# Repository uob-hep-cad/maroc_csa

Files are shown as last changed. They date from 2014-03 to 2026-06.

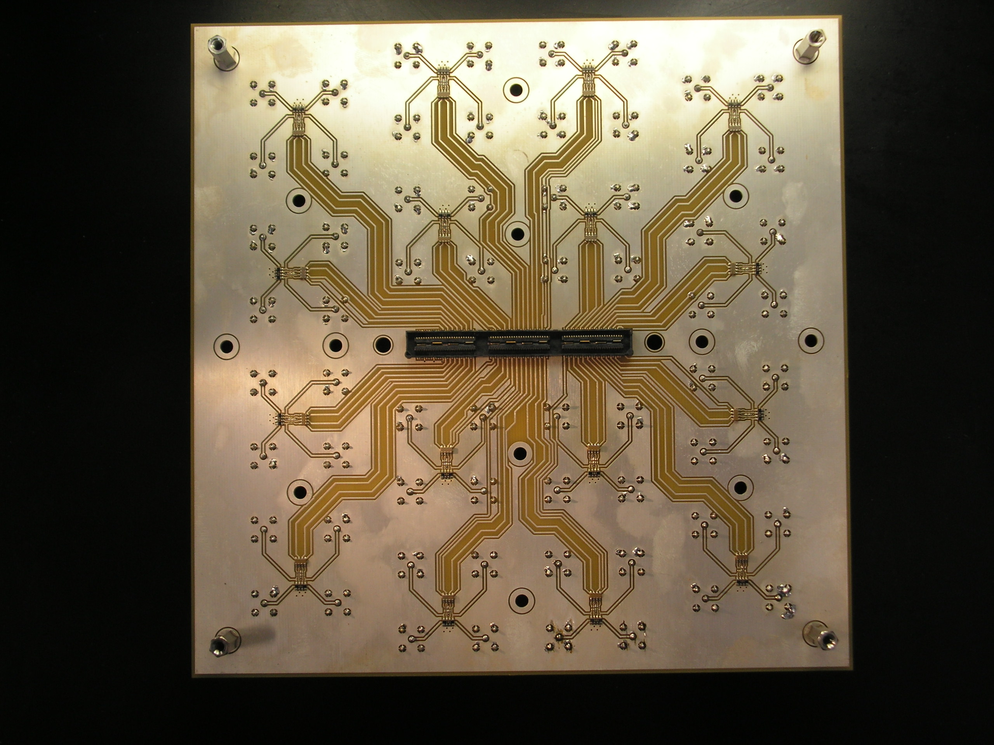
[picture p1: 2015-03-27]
www/Docs/Pictures/pc049a_lemo_adaptor_top_PICT1285.JPG

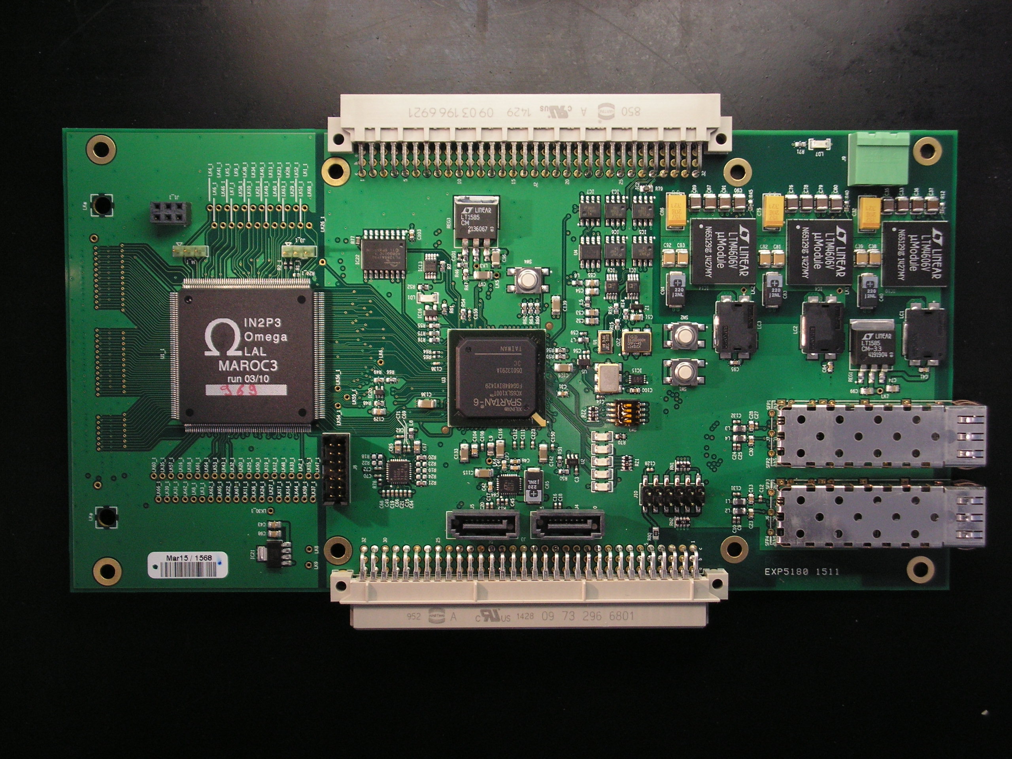
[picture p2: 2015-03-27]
www/Docs/Pictures/pc049a_top_PICT1282.JPG

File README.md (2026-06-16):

# PCB CAD and firmware for pc049a MAROC board

### Two firmware projects:
- `simple` - includes IPBus and MAROC control blocks
- `demo` - includes WhiteRabbit core - currently broken

### To build firmware
* Install Xilinx ISE and a command line environment where `hdlmake` ( from ohwr.org ) works
* pip install hdlmake
* cd firmware/syn/pc049a/simple
* hdlmake
* make

### Software to read out board (Python3)
* cd firmware/scripts
* ./takeMarocData.sh

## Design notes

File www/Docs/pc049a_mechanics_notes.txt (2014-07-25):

Lemo daughter-board
-------------------

Front pannel 3.0mm Aluminium sheet.

EPA connector is 14mm from end to PCB ( 17.0mm overall length )

Want surface flush with top of sheet, or slightly higher

So, stand-offs need to be ( 14mm - 3mm ) = 11mm or less.

For example, use RS 606-686 stand-offs ( M3, stud and thread, body 10mm long ) possibly with washer.

Put mounting holes with same spacing as for SQCD ( see http://www.samtec.com/documents/webfiles/cpdf/XQXX%20WITH%20SCREW-DOWN%20OPTIONS-MKT.pdf )

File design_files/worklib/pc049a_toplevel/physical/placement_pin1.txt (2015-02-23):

UUNITS = MILLIMETERS
SFP1                 19.0000        0.0000       90    TYCO_6367034-1      
SFP3                 0.0000         0.0000       90    TYCO_6367034-1      
SFP2                 21.3300       37.1000       90    TYCO_6367035-1      
SFP4                 2.3300        37.1000       90    TYCO_6367035-1      
IC16                 53.5250      119.4410      270    SOT23_5             
R79                  84.2010       66.6640       90    C0805               
R80                  1.2250        64.9000        0    C0805               
C138                 42.8500      117.6200      270    C0402               
IC21                 -4.8750      152.9000        0    SOT223_5            
R49                  38.9290      130.0970       90    C0603               
R66                  38.9300      127.1800       90    C0603               
R68                  -6.5120      154.6770      180  m C0603               
IC20                 35.1250      131.4000      270    SC70                
REG3                 68.5140      110.2610        0    TO254P1435X460-4N   
U3                   39.4420      102.8530       90    BGA484C100P22X22_2300X2300X260
U5                   44.5046       81.2202      180    SOT23-5             
J4                   4.2510        90.1620        0    SK_SATA_SMD_STR     
J5                   4.2510       110.1620        0    SK_SATA_SMD_STR     
U4                   71.9420       78.8530       90    SOIC8               
RG1_1                51.7900      159.3760       90  m SOT223_4            
R77                  72.5040      135.5830      180    C0402               
R75                  49.9500      116.9400       90    C0603               
R76                  48.3700      118.4300      270    C0603               
IC22                 73.3390      125.0110      180    SOIC127P1030X265-16N
C163                 72.2080       22.3576       90  m C0603               
C164                 72.3604       45.2938       90  m C0603               
C165                 71.7080       -0.4020       90  m C0603               
R11                  70.2014        1.1232       90  m C0603               
J9                   87.1250       10.9000      180    CON2MC_508          
R71                  94.7124       31.8064      270    C0603               
IC5                  72.0920       66.4480      180    SOIC127P600X175-8N  
IC6                  72.0920       72.9480      180    SOIC127P600X175-8N  
IC7                  76.2920       82.7580        0    SOIC127P600X175-8N  
IC2                  81.5920       66.4480      180    SOIC127P600X175-8N  
IC3                  81.5920       72.9480      180    SOIC127P600X175-8N  
REG1                 39.5920       16.0450        0    TO254P1435X460-4N   
C115                 16.8440      107.4090      270    C1206               
C116                 23.9320      102.0990      180    C1206               
C126                 41.9300       85.5200       90    C1206               
C133                 20.0430      110.6080        0    C1206               
C136                 33.3540      120.9980      270    C1206               
C139                 58.0950       88.8910      180    C1206               
C142                 19.9420       91.8530        0    C1206               
C96                  66.2710      103.1150        0    C1206               
C97                  63.7070      104.6630       90    C1206               
R69                  -1.8130      154.6770      180  m C0603               
C127                 39.4420       91.9030      270  m C0402               
C145                 39.4500       99.7550       90  m C0402               
C148                 36.4100      100.7700        0  m C0402               
C151                 55.9120       97.5740        0  m C0402               
C153                 29.6020      113.7830      180  m C0402               
C155                 46.3920      101.8530        0  m C0402               
C157                 42.4420       95.9030      270  m C0402               
C117                 42.4290      105.9090      180  m C0402               
C118                 39.4420      100.9030      270  m C0402               
C119                 39.4500      105.8510       90  m C0402               
R64                  45.4600      117.6200      270    C0402               
R65                  44.4500      117.6100      270    C0402               
C101                 67.5750      111.7510        0    C0402               
C3                   16.5550       83.9320        0    C0402               
C9                   4.8290        45.0010        0    C0402               
C10                  4.8290        46.0170        0    C0402               
C12                  10.8090       39.7940      180    C0402               
C24                  22.4130       46.1060        0    C0402               
C25                  22.4130       45.1060        0    C0402               
C27                  28.3350       40.9370      180    C0402               
C59                  49.9420       82.8030      270    C0402               
C71                  22.9340      124.8810      180    C0402               
C107                 30.4910      102.8610      180  m C0402               
C110                 30.4910       98.7970      180  m C0402               
C51                  53.8350       70.6630      270    C0805               
C52                  52.9420       81.2530      270    C0805               
C53                  54.9420       81.2530      270    C0805               
C54                  59.9420       81.2530      270    C0805               
C55                  61.9420       81.2530      270    C0805               
C65                  23.8840      126.3810      180    C0805               
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
LD7                  94.7886       24.8588       90    D1206               
LD6                  25.4320       79.4480      270    D1206               
LD4                  16.4320       79.4480      270    D1206               
LD3                  19.4320       79.4480      270    D1206               
RN1                  17.6150       59.6450      270    ARC241_SO8          
RN2                  4.1150        59.6450      270    ARC241_SO8          
RZ1                  17.9400       71.1940        0    ARC241_SO8          
RZ2                  29.7020       79.2180        0    ARC241_SO8          
R63                  55.1920       94.8530        0    C0603               
R61                  54.9560      115.3070        0    C0603               
R48                  33.3410      131.5970      270    C0603               
R67                  -3.3610      152.8990        0  m C0603               
R7                   66.6240      115.7630      180    C0603               
R56                  45.9420       88.6030      270    C0603               
R57                  38.8150       62.5900       90  m C0603               
R58                  47.4510       62.5900       90  m C0603               
R59                  44.4420       88.6030      270    C0603               
R60                  55.1920       93.3530        0    C0603               
R62                  55.1900       96.3700        0    C0603               
SW3                  29.2970       68.4020       90    SW_TYCO_1571983-4   
SW1                  42.8470       61.8110       90    OMRON_B3SN-3012     
SW2                  51.4830       61.8110       90    OMRON_B3SN-3012     
SW4                  64.5670       98.9180       90    OMRON_B3SN-3012     
R53                  35.4200      102.1200      270  m C0603               
IC15                 38.3170       68.0350       90    SON50P300X200X100-9N-R175X155
J10                  14.2390       54.7550       90    SAMTEC_TSM-106-01-X-DV
LD2                  22.4320       79.4480      270    D1206               
LD5                  13.4320       79.4480      270    D1206               
LD1                  58.4020      120.8370      270    D1206               
R70                  25.4320       72.6980       90    C0603               
R52                  60.9130      121.0100      270    C0603               
R50                  17.0050       87.6820      270    C0603               
C34                  79.7398        0.5764        0  m C0603               
C88                  80.2906       46.2504        0  m C0603               
J1                   70.7450      198.9860      270  m CON150_QTSDA        
R44                  70.7602       46.7924       90  m C0603               
R51                  20.2550       87.9320      180    C0603               
R46                  66.1200      111.7390      270    C0603               
R47                  64.6600      110.2400      180    C0603               
U2                   20.7496       83.9922      180    SOT23-5             
R32                  29.0570       84.7100        0  m C0603               
R34                  27.8070       86.4600      270  m C0603               
R26                  35.9380       84.7100        0  m C0603               
R28                  34.4380       83.2100        0  m C0603               
R30                  32.0570       84.7100        0  m C0603               
R33                  29.3070       86.4600      270  m C0603               
R35                  25.8070       87.9600      270  m C0603               
R3                   37.4060       83.1760        0  m C0603               
R25                  35.6880       86.4600      270  m C0603               
R27                  34.1880       86.4600      270  m C0603               
R29                  32.6880       86.4600      270  m C0603               
R31                  30.8070       86.4600      270  m C0603               
QZ1                  36.8760       74.3480        0    OSC_SILABS_SI570    
IC1                  58.8330       71.6190        0    SOP65P490X95-8N     
IC9                  58.8330       76.6190        0    SOP65P490X95-8N     
J8                   23.9480      142.0290      270    CON14MD_2MM         
L5                   56.6920       81.3530        0    C0603               
L6                   61.9420       83.1030       90    C0603               
L7                   48.4420       81.6030       90    C0603               
L8                   25.4960      123.2380        0    C0603               
Z1                   55.4460       70.7028        0    SOT23               
QZ2                  45.8720       72.3270        0    OSCSC254P490X696X180-6N
U1                   46.1480       75.9940       90    OSC_4PIN_53S        
R54                  55.3110      110.8530      180    C0603               
R55                  51.7600      118.4300      270    C0603               
R20                  20.4000      120.0600       90    C0603               
R21                  14.3000      120.0600       90    C0603               
R14                  55.3450       72.3060      180    C0603               
R15                  51.4000       74.2860        0    C0603               
R16                  55.1150       74.5920        0    C0603               
R17                  50.6540       67.2260        0  m C0603               
IC11                 14.6110      127.9800        0    QFN50P500X500X100-33N-S355
LC1                  56.0306       -1.2950      180    MURATA_BNX02        
LC3                  57.7324       44.1202      180    MURATA_BNX02        
LC2                  57.5800       23.3430      180    MURATA_BNX02        
C44                  9.2820       102.6070        0    C0402               
C103                 73.9390      122.9560      180    C0603               
C100                 36.4320       70.7850      270    C0603               
C31                  35.6400       87.9900      270    C0603               
C48_1                54.1550      153.2895      270  m C0603               
C52_1                61.5256      146.4027      270  m C0603               
C53_1                19.4830      150.3896      180  m C0603               
C54_1                50.1699      151.2392      180  m C0603               
C48                  19.5100       97.7900       90    C0603               
C41                  41.3470        1.5550      270    C0603               
C95                  43.0488       46.9448      270    C0603               
C84                  41.2896       23.3510        0    C0603               
C42                  14.1570      104.4370      180    C0603               
C46                  17.9870       97.7930       90    C0603               
C13                  11.1090       42.0800      180    C0603               
C23                  6.0530        42.0800        0    C0603               
C28                  28.6350       42.2070      180    C0603               
C30                  23.5790       42.2070        0    C0603               
C47                  19.3100      101.1500      180    C0603               
C33                  81.8518        6.9660      180    CAPC3225X279N       
C35                  81.8360       10.4316      180    CAPC3225X279N       
C36                  81.8574        3.4302      180    CAPC3225X279N       
C37                  81.8614       -0.0586      180    CAPC3225X279N       
C87                  82.4056       52.6154      180    CAPC3225X279N       
C89                  82.4056       56.1154      180    CAPC3225X279N       
C90                  82.4056       45.6154      180    CAPC3225X279N       
C91                  82.4056       49.1154      180    CAPC3225X279N       
C76                  82.2424       33.1900      180    CAPC3225X279N       
C78                  82.2678       29.6848      180    CAPC3225X279N       
C79                  82.2678       26.1796      180    CAPC3225X279N       
C80                  82.2678       22.6744      180    CAPC3225X279N       
C38                  70.7348       16.4274      270    C1210               
C39                  66.7470       16.4274      270    C1210               
C92                  67.2630       62.0700      270    C1210               
C93                  71.3270       62.0700      270    C1210               
C81                  71.1412       39.1858      270    C1210               
C82                  67.1280       39.1604      270    C1210               
J6                   3.7300        26.8000       90    TYCO_1367073        
J7                   22.7300       26.8000       90    TYCO_1367073        
IC13                 68.0580      117.5590      180    SOP65P490X110-8N    
C32                  75.3576       14.9528        0    C7343POL            
C86                  75.9056       60.6154        0    C7343POL            
C75                  75.7386       37.6858        0    C7343POL            
C40                  63.1816       14.7726      180    POSCAP_D3           
C94                  63.4530       60.4430      180    POSCAP_D3           
C83                  63.4102       37.5056      180    POSCAP_D3           
C85                  10.6210       94.0980        0    POSCAP_D3           
L9                   23.3420      104.3530      180    INDC2012X90N        
L1                   9.7240        45.7740      270    INDC2012X90N        
L2                   7.4380        43.9740       90    INDC2012X90N        
L3                   27.2500       45.9010      270    INDC2012X90N        
L4                   24.9640       44.1010       90    INDC2012X90N        
RG1                  11.9912      101.7674        0    QFN50P400X500X80-29N-R375X275
IC10                 68.9314        3.6244      270    LGA133S127P12X12_05-08-1766
IC14                 69.4902       49.2936      270    LGA133S127P12X12_05-08-1766
IC4                  69.3378       26.3574      270    LGA133S127P12X12_05-08-1766
R13                  10.1820      101.5910      180    C0402               
R72                  66.8940       20.0570      180  m C0603               
R73                  67.0210       43.0440      180  m C0603               
R74                  66.3860       -2.6760      180  m C0603               
R10                  75.8910        2.3932       90  m C0603               
R43                  76.4498       48.0624       90  m C0603               
R38                  76.2974       25.1262       90  m C0603               
R12                  80.5526       -2.8272      180    C0603               
R45                  81.1114       42.8420      180    C0603               
R40                  80.9590       19.9058      180    C0603               
R18                  20.6500      132.1400      270    C0603               
R19                  17.3400      120.0600       90    C0603               
R22                  19.1220      132.1110      270    C0603               
R23                  18.8680      120.0700       90    C0603               
R24                  15.8200      120.0700       90    C0603               
R8                   76.7600       -1.3000        0  m C0603               
R9                   75.2760       -2.8030      180  m C0603               
R41                  77.2840       44.4410        0  m C0603               
R42                  75.7840       42.9170      180  m C0603               
R36                  77.1744       21.5060        0  m C0603               
R37                  75.6800       20.0000      180  m C0603               
R39                  70.6078       23.8562       90  m C0603               
LK1                  60.1684       21.3028        0    1-HOLE_0-8P         
LK2                  60.2954       44.2390        0    1-HOLE_0-8P         
LK3                  65.8660      107.6870        0    1-HOLE_0-8P         
LK4                  19.5900      104.6700        0    1-HOLE_0-8P         
LK5                  63.7070      102.9880        0    1-HOLE_0-8P         
LK6                  43.1330      130.4200        0    1-HOLE_0-8P         
LK7                  36.2750       11.2940        0    1-HOLE_0-8P         
LK8                  -1.5790      147.7440        0    1-HOLE_0-8P         
LK9                  -5.3890      147.8710        0    1-HOLE_0-8P         
LK1_1                79.5470      148.2455        0    1-HOLE_0-8P         
LK2_1                16.0470      149.7695        0    1-HOLE_0-8P         
LK3_1                10.4590      173.1375        0    1-HOLE_0-8P         
LK4_1                79.5470      170.5975        0    1-HOLE_0-8P         
LK5_1                79.5470      166.5335        0    1-HOLE_0-8P         
LK6_1                75.4830      169.5815        0    1-HOLE_0-8P         
LK7_1                75.4830      165.5175        0    1-HOLE_0-8P         
LK8_1                10.4590      175.1695        0    1-HOLE_0-8P         
LK9_1                79.5470      164.5015        0    1-HOLE_0-8P         
LK10_1               75.4830      161.4535        0    1-HOLE_0-8P         
LK11_1               10.4590      162.9775        0    1-HOLE_0-8P         
LK12_1               16.0470      155.8655        0    1-HOLE_0-8P         
LK13_1               79.5470      156.3735        0    1-HOLE_0-8P         
LK14_1               10.4590      152.8175        0    1-HOLE_0-8P         
LK15_1               16.0470      147.7375        0    1-HOLE_0-8P         
LK16_1               16.0470      178.2175        0    1-HOLE_0-8P         
LK17_1               10.4590      154.8495        0    1-HOLE_0-8P         
LK18_1               16.0470      176.1855        0    1-HOLE_0-8P         
LK19_1               16.0470      157.8975        0    1-HOLE_0-8P         
LK20_1               16.0470      163.9935        0    1-HOLE_0-8P         
LK21_1               75.4830      159.4215        0    1-HOLE_0-8P         
LK22_1               10.4590      167.0415        0    1-HOLE_0-8P         
LK23_1               79.5470      154.3415        0    1-HOLE_0-8P         
LK24_1               10.4590      158.9135        0    1-HOLE_0-8P         
LK25_1               16.0470      161.9615        0    1-HOLE_0-8P         
LK26_1               66.8470      144.1035        0    1-HOLE_0-8P         
LK27_1               10.4590      156.8815        0    1-HOLE_0-8P         
LK28_1               79.5470      152.3095        0    1-HOLE_0-8P         
LK29_1               75.4830      151.2935        0    1-HOLE_0-8P         
LK30_1               7.6650       156.8815        0    1-HOLE_0-8P         
LK31_1               10.4590      179.4875        0    1-HOLE_0-8P         
LK32_1               16.0470      166.0255        0    1-HOLE_0-8P         
LK33_1               16.0470      151.8015        0    1-HOLE_0-8P         
LK34_1               79.5470      160.4375        0    1-HOLE_0-8P         
LK35_1               16.0470      182.5355        0    1-HOLE_0-8P         
LK36_1               10.4590      160.9455        0    1-HOLE_0-8P         
LK37_1               10.4590      146.7215        0    1-HOLE_0-8P         
LK38_1               79.5470      162.4695        0    1-HOLE_0-8P         
LK39_1               10.4590      181.5195        0    1-HOLE_0-8P         
LK40_1               75.4830      155.3575        0    1-HOLE_0-8P         
LK41_1               79.5470      168.5655        0    1-HOLE_0-8P         
LK42_1               10.4590      177.2015        0    1-HOLE_0-8P         
LK43_1               16.0470      168.0575        0    1-HOLE_0-8P         
LK44_1               10.4590      150.7855        0    1-HOLE_0-8P         
LK45_1               79.5470      158.4055        0    1-HOLE_0-8P         
LK46_1               75.4830      167.5495        0    1-HOLE_0-8P         
LK47_1               16.0470      145.7055        0    1-HOLE_0-8P         
LK48_1               16.0470      153.8335        0    1-HOLE_0-8P         
LK49_1               75.4830      157.3895        0    1-HOLE_0-8P         
LK50_1               16.0470      159.9295        0    1-HOLE_0-8P         
LK51_1               75.4830      149.2615        0    1-HOLE_0-8P         
LK52_1               79.5470      150.2775        0    1-HOLE_0-8P         
LK53_1               16.0470      170.0895        0    1-HOLE_0-8P         
LK54_1               32.8110      140.6255        0    1-HOLE_0-8P         
LK55_1               34.8430      138.4665        0    1-HOLE_0-8P         
LK56_1               36.8750      140.6255        0    1-HOLE_0-8P         
LK57_1               16.0470      180.5035        0    1-HOLE_0-8P         
LK58_1               75.4830      163.4855        0    1-HOLE_0-8P         
LK59_1               10.4590      148.7535        0    1-HOLE_0-8P         
LK60_1               16.0470      184.5675        0    1-HOLE_0-8P         
LK61_1               16.0470      174.1535        0    1-HOLE_0-8P         
LK62_1               10.4590      171.1055        0    1-HOLE_0-8P         
LK63_1               75.4830      153.3255        0    1-HOLE_0-8P         
LK64_1               16.0470      172.1215        0    1-HOLE_0-8P         
LK65_1               10.4590      169.0735        0    1-HOLE_0-8P         
LK66_1               10.4590      183.5515        0    1-HOLE_0-8P         
LK67_1               10.4590      165.0095        0    1-HOLE_0-8P         
LK68_1               75.4830      147.2295        0    1-HOLE_0-8P         
C49                  12.3330      128.8210      180    C0402               
C1                   64.1650      117.5410        0  m C0402               
C2                   76.8920       70.3530        0  m C0402               
C4                   73.5470      126.2810        0  m C0402               
C5                   80.9920       82.8530      180  m C0402               
C6                   67.3920       72.8530        0  m C0402               
C7                   71.3850       83.9380      180  m C0402               
C8                   66.8920       78.8530        0  m C0402               
C14                  34.9420       77.9030       90    C0402               
C15                  12.3400      124.7400      180    C0402               
C16                  8.2660        88.8910        0    C0402               
C17                  8.3930       104.1310        0    C0402               
C18                  8.2660        87.8750        0    C0402               
C19                  12.3330      127.8050      180    C0402               
C20                  8.3010       105.1620        0    C0402               
C21                  12.3330      125.7730      180    C0402               
C45                  9.2820       100.5750        0    C0402               
C60                  49.2000       75.9890      180  m C0402               
C61                  16.8360      120.7510      270  m C0402               
C77                  79.8462       23.3094        0  m C0402               
C128                 17.4420       65.9030       90    C0402               
C130                 47.4510       87.4250      270  m C0402               
C131                 11.5760       45.1730       90    C0402               
C132                 28.9420       45.3000       90    C0402               
C134                 32.4420      106.9030      270  m C0402               
C137                 42.4920      102.8530      180  m C0402               
C140                 40.4500      107.7560       90  m C0402               
C141                 39.8310       88.3140      270  m C0402               
C143                 44.3450      113.7830        0  m C0402               
C144                 31.9570      116.0110       90  m C0402               
C146                 50.4610       92.9880      270  m C0402               
C147                 34.7510      116.0110       90  m C0402               
C149                 23.3790      102.0990      180  m C0402               
C150                 22.3630       89.6530        0    C0402               
C152                 50.3630      102.8690        0  m C0402               
C154                 32.4920      102.8530      180  m C0402               
C156                 37.6030      113.7830      180  m C0402               
C158                 26.1150       95.8180       90  m C0402               
C159                 55.0200      109.3680      180    C0402               
C160                 40.4660      108.8880      270  m C0402               
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
J3_1                 69.3870      152.0555      270    CONHE13D3X1M        
J4_1                 69.3870      177.7095      270    CONHE13D3X1M        
J1_1                 76.9850      176.4995      270    SAMTEC_SSW-103-01-G-D
J2                   95.3650      139.7200        0    HARTING_0903196X921 
J3                   -9.1150       50.8200      180    HARTING_09732966801 
D1_1                 52.8550      148.7395        0  m SOD323_INV          
U1_1                 59.4950      178.9795      270    PQFP240_050         
R20_1                33.0450      157.6995      180  m C0402               
R21_1                35.9450      157.6995        0  m C0402               
R22_1                33.0450      159.6995      180  m C0402               
R23_1                35.9450      159.6995        0  m C0402               
R25_1                31.0324      165.1165      180  m C0402               
R26_1                23.5450      165.1995      180  m C0402               
R28_1                33.9450      162.6995        0  m C0402               
R29_1                35.9450      162.6995        0  m C0402               
R30_1                24.4450      161.1995        0  m C0402               
R31_1                23.5450      162.1995      180  m C0402               
R32_1                31.0476      153.2569      180  m C0402               
R33_1                31.9476      152.0109        0  m C0402               
R34_1                54.4450      171.6995        0  m C0402               
R35_1                53.5450      170.6995      180  m C0402               
R36_1                31.0246      147.7191      180  m C0402               
R37_1                23.5443      148.1433      180  m C0402               
R14_1                35.0625      161.6673      180  m C0402               
R17_1                55.9450      158.6995        0  m C0402               
R78                  14.1400      130.7600        0    C0402               
R1                   81.9420       68.8030       90  m C0402               
R2                   81.9420       75.3030       90  m C0402               
R6                   72.5970       79.9430       90  m C0402               
R24_1                63.7990      150.7275      270    C0402               
R3_1                 58.7835      147.9388        0  m C0402               
R4_1                 23.5443      150.5662      180  m C0402               
R5_1                 31.0476      163.9055      180  m C0402               
R6_1                 56.8478      174.7564        0  m C0402               
R7_1                 55.9450      169.1995        0  m C0402               
R8_1                 31.0450      173.6995      180  m C0402               
R9_1                 55.9353      167.8937        0  m C0402               
R10_1                32.9763      167.1576      180  m C0402               
R11_1                55.9864      166.0878        0  m C0402               
R12_1                24.4450      157.1995        0  m C0402               
R13_1                55.9450      161.6995        0  m C0402               
R15_1                24.4450      154.6995        0  m C0402               
R16_1                24.4450      152.6995        0  m C0402               
R27_1                34.0050      151.3895      180  m C0402               
R46_1                62.9743      146.7405      270  m C0402               
R47_1                19.7509      149.0089      180  m C0402               
R4                   72.2850       82.6680        0  m C0402               
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

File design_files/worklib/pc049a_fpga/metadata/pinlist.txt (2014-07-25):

(Pinlist
	(Pin
		(Name ENABLE_GCLK_DRIVE_O)
		(MSB )
		(LSB )
		(Type OUTPUT)
		(Location Right)
		(InputLoadLow )
		(InputLoadHigh )
		(OutputLoadLow 1.0)
		(OutputLoadHigh -1.0)
		(CheckLoad Both)
		(CheckIO Both)
		(CheckDir 1)
		(CheckAssert 1)
		(CheckOutput 1)
		(UnknownLoading 0)
		(PinShape Line)
		(DIFF_PAIR_PINS_POS )
		(DIFF_PAIR_PINS_NEG )
	)

	(Pin
		(Name ENABLE_GLOBALTRIG_DRIVE_O)
		(MSB )
		(LSB )
		(Type OUTPUT)
		(Location Right)
		(InputLoadLow )
		(InputLoadHigh )
		(OutputLoadLow 1.0)
		(OutputLoadHigh -1.0)
		(CheckLoad Both)
		(CheckIO Both)
		(CheckDir 1)
		(CheckAssert 1)
		(CheckOutput 1)
		(UnknownLoading 0)
		(PinShape Line)
		(DIFF_PAIR_PINS_POS )
		(DIFF_PAIR_PINS_NEG )
	)

	(Pin
		(Name LVDS_GCLK_FROM_FPGA_N_O)
		(MSB )
		(LSB )
		(Type OUTPUT)
		(Location Right)
		(InputLoadLow -0.01)
		(InputLoadHigh 0.01)
		(OutputLoadLow 1.0)
		(OutputLoadHigh -1.0)
		(CheckLoad Both)
		(CheckIO Both)
		(CheckDir 1)
		(CheckAssert 1)
		(CheckOutput 1)
		(UnknownLoading 0)
		(PinShape Line)
		(DIFF_PAIR_PINS_POS )
		(DIFF_PAIR_PINS_NEG )
	)

	(Pin
		(Name LVDS_GCLK_FROM_FPGA_P_O)
		(MSB )
		(LSB )
		(Type OUTPUT)
		(Location Right)
		(InputLoadLow )
		(InputLoadHigh )
		(OutputLoadLow 1.0)
		(OutputLoadHigh -1.0)
		(CheckLoad Both)
		(CheckIO Both)
		(CheckDir 1)
		(CheckAssert 1)
		(CheckOutput 1)
		(UnknownLoading 0)
		(PinShape Line)
		(DIFF_PAIR_PINS_POS )
		(DIFF_PAIR_PINS_NEG )
	)

	(Pin
		(Name LVDS_GCLK_TO_FPGA_N_I)
		(MSB )
		(LSB )
		(Type INPUT)
		(Location Left)
		(InputLoadLow -0.01)
		(InputLoadHigh 0.01)
		(OutputLoadLow )
		(OutputLoadHigh )
		(CheckLoad Off)
		(CheckIO Off)
		(CheckDir 0)
		(CheckAssert 0)
		(CheckOutput 0)
		(UnknownLoading 0)
		(PinShape Line)
		(DIFF_PAIR_PINS_POS )
		(DIFF_PAIR_PINS_NEG )
	)

	(Pin
		(Name LVDS_GCLK_TO_FPGA_P_I)
		(MSB )
		(LSB )
		(Type INPUT)
		(Location Left)
		(InputLoadLow -0.01)
		(InputLoadHigh 0.01)
		(OutputLoadLow )
		(OutputLoadHigh )
		(CheckLoad Both)
		(CheckIO Both)
		(CheckDir 1)
		(CheckAssert 1)
		(CheckOutput 1)
		(UnknownLoading 0)
		(PinShape Line)
		(DIFF_PAIR_PINS_POS )
		(DIFF_PAIR_PINS_NEG )
	)

	(Pin
		(Name LVDS_GLOBALTRIG_FROM_FPGA_N_O)
		(MSB )
		(LSB )
		(Type OUTPUT)
		(Location Right)
		(InputLoadLow -0.01)
		(InputLoadHigh 0.01)
		(OutputLoadLow 1.0)
		(OutputLoadHigh -1.0)
		(CheckLoad Both)
		(CheckIO Both)
		(CheckDir 1)
		(CheckAssert 1)
		(CheckOutput 1)
		(UnknownLoading 0)
		(PinShape Line)
		(DIFF_PAIR_PINS_POS )
		(DIFF_PAIR_PINS_NEG )
	)

	(Pin
		(Name LVDS_GLOBALTRIG_FROM_FPGA_P_O)
		(MSB )
		(LSB )
		(Type OUTPUT)
		(Location Right)
		(InputLoadLow )
		(InputLoadHigh )
		(OutputLoadLow 1.0)
		(OutputLoadHigh -1.0)
		(CheckLoad Both)
		(CheckIO Both)
		(CheckDir 1)
		(CheckAssert 1)
		(CheckOutput 1)
		(UnknownLoading 0)
		(PinShape Line)
		(DIFF_PAIR_PINS_POS )
		(DIFF_PAIR_PINS_NEG )
	)

	(Pin
		(Name LVDS_GLOBALTRIG_TO_FPGA_N_I)
		(MSB )
		(LSB )
		(Type INPUT)
		(Location Left)
		(InputLoadLow -0.01)
		(InputLoadHigh 0.01)
		(OutputLoadLow )
		(OutputLoadHigh )
		(CheckLoad Both)
		(CheckIO Both)
		(CheckDir 1)
		(CheckAssert 1)
		(CheckOutput 1)
		(UnknownLoading 0)
		(PinShape Line)
		(DIFF_PAIR_PINS_POS )
		(DIFF_PAIR_PINS_NEG )
	)

	(Pin
		(Name LVDS_GLOBALTRIG_TO_FPGA_P_I)
		(MSB )
		(LSB )
		(Type INPUT)
		(Location Left)
		(InputLoadLow -0.01)
		(InputLoadHigh 0.01)
		(OutputLoadLow )
		(OutputLoadHigh )
		(CheckLoad Both)
		(CheckIO Both)
		(CheckDir 1)
		(CheckAssert 1)
		(CheckOutput 1)
		(UnknownLoading 0)
		(PinShape Line)
		(DIFF_PAIR_PINS_POS )
		(DIFF_PAIR_PINS_NEG )
	)

	(Pin
		(Name LVDS_OTRIG_FROM_FPGA_N_O)
		(MSB )
		(LSB )
		(Type OUTPUT)
		(Location Right)
		(InputLoadLow -0.01)
		(InputLoadHigh 0.01)
		(OutputLoadLow 1.0)
		(OutputLoadHigh -1.0)
		(CheckLoad Both)
		(CheckIO Both)
		(CheckDir 1)
		(CheckAssert 1)
		(CheckOutput 1)
		(UnknownLoading 0)
		(PinShape Line)
		(DIFF_PAIR_PINS_POS )
		(DIFF_PAIR_PINS_NEG )
	)

	(Pin
		(Name LVDS_OTRIG_FROM_FPGA_P_O)
		(MSB )
		(LSB )
		(Type OUTPUT)
		(Location Right)
		(InputLoadLow )
		(InputLoadHigh )
		(OutputLoadLow 1.0)
		(OutputLoadHigh -1.0)
		(CheckLoad Both)
		(CheckIO Both)
		(CheckDir 1)
		(CheckAssert 1)
		(CheckOutput 1)
		(UnknownLoading 0)
		(PinShape Line)
		(DIFF_PAIR_PINS_POS )
		(DIFF_PAIR_PINS_NEG )
	)

	(Pin
		(Name LVDS_OTRIG_TO_FPGA_N_I)
		(MSB )
		(LSB )
		(Type INPUT)
		(Location Left)
		(InputLoadLow -0.01)
		(InputLoadHigh 0.01)
		(OutputLoadLow )
		(OutputLoadHigh )
		(CheckLoad Off)
		(CheckIO Off)
		(CheckDir 0)
		(CheckAssert 0)
		(CheckOutput 0)
		(UnknownLoading 0)
		(PinShape Line)
		(DIFF_PAIR_PINS_POS )
		(DIFF_PAIR_PINS_NEG )
	)

	(Pin
		(Name LVDS_OTRIG_TO_FPGA_P_I)
		(MSB )
		(LSB )
		(Type INPUT)
		(Location Left)
		(InputLoadLow -0.01)
		(InputLoadHigh 0.01)
		(OutputLoadLow )
		(OutputLoadHigh )
		(CheckLoad Both)
		(CheckIO Both)
		(CheckDir 1)
		(CheckAssert 1)
		(CheckOutput 1)
		(UnknownLoading 0)
		(PinShape Line)
		(DIFF_PAIR_PINS_POS )
		(DIFF_PAIR_PINS_NEG )
	)

	(Pin
		(Name BUTTON1_I)
		(MSB )
		(LSB )
		(Type INPUT)
		(Location Left)
		(InputLoadLow -0.01)
		(InputLoadHigh 0.01)
		(OutputLoadLow )
		(OutputLoadHigh )
		(CheckLoad Both)
		(CheckIO Both)
		(CheckDir 1)
		(CheckAssert 1)
		(CheckOutput 1)
		(UnknownLoading 0)
		(PinShape Line)
		(DIFF_PAIR_PINS_POS )
		(DIFF_PAIR_PINS_NEG )
	)

	(Pin
		(Name BUTTON2_I)
		(MSB )
		(LSB )
		(Type INPUT)
		(Location Left)
		(InputLoadLow -0.01)
		(InputLoadHigh 0.01)
		(OutputLoadLow )
		(OutputLoadHigh )
		(CheckLoad Both)
		(CheckIO Both)
		(CheckDir 1)
		(CheckAssert 1)
		(CheckOutput 1)
		(UnknownLoading 0)
		(PinShape Line)
		(DIFF_PAIR_PINS_POS )
		(DIFF_PAIR_PINS_NEG )
	)

	(Pin
		(Name FPGA_SCL_B)
		(MSB )
		(LSB )
		(Type BIDIR)
		(Location Right)
		(InputLoadLow -0.01)
		(InputLoadHigh 0.01)
		(OutputLoadLow 1.0)
		(OutputLoadHigh -1.0)
		(CheckLoad Both)
		(CheckIO Both)
		(CheckDir 1)
		(CheckAssert 1)
		(CheckOutput 1)
		(UnknownLoading 0)
		(PinShape Line)
		(DIFF_PAIR_PINS_POS )
		(DIFF_PAIR_PINS_NEG )
	)

	(Pin
		(Name FPGA_SDA_B)
		(MSB )
		(LSB )
		(Type BIDIR)
		(Location Right)
		(InputLoadLow -0.01)
		(InputLoadHigh 0.01)
		(OutputLoadLow 1.0)
		(OutputLoadHigh -1.0)
		(CheckLoad Both)
		(CheckIO Both)
		(CheckDir 1)
		(CheckAssert 1)
		(CheckOutput 1)
		(UnknownLoading 0)
		(PinShape Line)
		(DIFF_PAIR_PINS_POS )
		(DIFF_PAIR_PINS_NEG )
	)

	(Pin
		(Name CTEST_O)
		(MSB 5)
		(LSB 0)
		(Type OUTPUT)
		(Location Right)
		(InputLoadLow )
		(InputLoadHigh )
		(OutputLoadLow 1.0)
		(OutputLoadHigh -1.0)
		(CheckLoad Both)
		(CheckIO Both)
		(CheckDir 1)
		(CheckAssert 1)
		(CheckOutput 1)
		(UnknownLoading 0)
		(PinShape Line)
		(DIFF_PAIR_PINS_POS )
		(DIFF_PAIR_PINS_NEG )
	)

	(Pin
		(Name LEDS_O)
		(MSB 4)
		(LSB 0)
		(Type OUTPUT)
		(Location Right)
		(InputLoadLow )
		(InputLoadHigh )
		(OutputLoadLow 1.0)
		(OutputLoadHigh -1.0)
		(CheckLoad Both)
		(CheckIO Both)
		(CheckDir 1)
		(CheckAssert 1)
		(CheckOutput 1)
		(UnknownLoading 0)
		(PinShape Line)
		(DIFF_PAIR_PINS_POS )
		(DIFF_PAIR_PINS_NEG )
	)

	(Pin
		(Name DIP_SWITCH_I)
		(MSB 3)
		(LSB 0)
		(Type INPUT)
		(Location Left)
		(InputLoadLow -0.01)
		(InputLoadHigh 0.01)
		(OutputLoadLow )
		(OutputLoadHigh )
		(CheckLoad Both)
		(CheckIO Both)
		(CheckDir 1)
		(CheckAssert 1)
		(CheckOutput 1)
		(UnknownLoading 0)
		(PinShape Line)
		(DIFF_PAIR_PINS_POS )
		(DIFF_PAIR_PINS_NEG )
	)

	(Pin
		(Name GPIO)
		(MSB 7)
		(LSB 0)
		(Type OUTPUT)
		(Location Right)
		(InputLoadLow )
		(InputLoadHigh )
		(OutputLoadLow 1.0)
		(OutputLoadHigh -1.0)
		(CheckLoad Both)
		(CheckIO Both)
		(CheckDir 1)
		(CheckAssert 1)
		(CheckOutput 1)
		(UnknownLoading 0)
		(PinShape Line)
		(DIFF_PAIR_PINS_POS )
		(DIFF_PAIR_PINS_NEG )
	)

	(Pin
		(Name ONE_WIRE_B)
		(MSB )
		(LSB )
		(Type BIDIR)
		(Location Right)
		(InputLoadLow -0.01)
		(InputLoadHigh 0.01)
		(OutputLoadLow 1.0)
		(OutputLoadHigh -1.0)
		(CheckLoad Both)
		(CheckIO Both)
		(CheckDir 1)
		(CheckAssert 1)
		(CheckOutput 1)
		(UnknownLoading 0)
		(PinShape Line)
		(DIFF_PAIR_PINS_POS )
		(DIFF_PAIR_PINS_NEG )
	)

	(Pin
		(Name CLK_20M_VCXO_I)
		(MSB )
		(LSB )
		(Type INPUT)
		(Location Left)
		(InputLoadLow -0.01)
		(InputLoadHigh 0.01)
		(OutputLoadLow )
		(OutputLoadHigh )
		(CheckLoad Both)
		(CheckIO Both)
		(CheckDir 1)
		(CheckAssert 1)
		(CheckOutput 1)
		(UnknownLoading 0)
		(PinShape )
		(DIFF_PAIR_PINS_POS )
		(DIFF_PAIR_PINS_NEG )
	)

	(Pin
		(Name CLK_125M_PLLREF_N_I)
		(MSB )
		(LSB )
		(Type INPUT)
		(Location Left)
		(InputLoadLow -0.01)
		(InputLoadHigh 0.01)
		(OutputLoadLow )
		(OutputLoadHigh )
		(CheckLoad Off)
		(CheckIO Off)
		(CheckDir 0)
		(CheckAssert 0)
		(CheckOutput 0)
		(UnknownLoading 0)
		(PinShape )
		(DIFF_PAIR_PINS_POS )
		(DIFF_PAIR_PINS_NEG )
	)

	(Pin
		(Name CLK_125M_PLLREF_P_I)
		(MSB )
		(LSB )
		(Type INPUT)
		(Location Left)
		(InputLoadLow -0.01)
		(InputLoadHigh 0.01)
		(OutputLoadLow )
		(OutputLoadHigh )
		(CheckLoad Both)
		(CheckIO Both)
		(CheckDir 1)
		(CheckAssert 1)
		(CheckOutput 1)
		(UnknownLoading 0)
		(PinShape )
		(DIFF_PAIR_PINS_POS )
		(DIFF_PAIR_PINS_NEG )
	)

	(Pin
		(Name PLL25DAC1_SYNC_N_O)
		(MSB )
		(LSB )
		(Type OUTPUT)
		(Location Right)
		(InputLoadLow )
		(InputLoadHigh )
		(OutputLoadLow 1.0)
		(OutputLoadHigh -1.0)
		(CheckLoad Both)
		(CheckIO Both)
		(CheckDir 1)
		(CheckAssert 1)
		(CheckOutput 1)
		(UnknownLoading 0)
		(PinShape )
		(DIFF_PAIR_PINS_POS )
		(DIFF_PAIR_PINS_NEG )
	)

	(Pin
		(Name PLL25DAC2_SYNC_N_O)
		(MSB )
		(LSB )
		(Type OUTPUT)
		(Location Right)
		(InputLoadLow )
		(InputLoadHigh )
		(OutputLoadLow 1.0)
		(OutputLoadHigh -1.0)
		(CheckLoad Both)
		(CheckIO Both)
		(CheckDir 1)
		(CheckAssert 1)
		(CheckOutput 1)
		(UnknownLoading 0)
		(PinShape )
		(DIFF_PAIR_PINS_POS )
		(DIFF_PAIR_PINS_NEG )
	)

	(Pin
		(Name PLL25DAC_DIN_O)
		(MSB )
		(LSB )
		(Type OUTPUT)
		(Location Right)
		(InputLoadLow )
		(InputLoadHigh )
		(OutputLoadLow 1.0)
		(OutputLoadHigh -1.0)
		(CheckLoad Both)
		(CheckIO Both)
		(CheckDir 1)
		(CheckAssert 1)
		(CheckOutput 1)
		(UnknownLoading 0)
		(PinShape )
		(DIFF_PAIR_PINS_POS )
		(DIFF_PAIR_PINS_NEG )
	)

	(Pin
		(Name PLL25DAC_SCLK_O)
		(MSB )
		(LSB )
		(Type OUTPUT)
		(Location Right)
		(InputLoadLow )
		(InputLoadHigh )
		(OutputLoadLow 1.0)
		(OutputLoadHigh -1.0)
		(CheckLoad Both)
		(CheckIO Both)
		(CheckDir 1)
		(CheckAssert 1)
		(CheckOutput 1)
		(UnknownLoading 0)
		(PinShape )
		(DIFF_PAIR_PINS_POS )
		(DIFF_PAIR_PINS_NEG )
	)

	(Pin
		(Name SI57X_CLK_N_I)
		(MSB )
		(LSB )
		(Type UNSPEC)
		(Location Left)
		(InputLoadLow )
		(InputLoadHigh )
		(OutputLoadLow )
		(OutputLoadHigh )
		(CheckLoad Off)
		(CheckIO Off)
		(CheckDir 0)
		(CheckAssert 0)
		(CheckOutput 0)
		(UnknownLoading 0)
		(PinShape )
		(DIFF_PAIR_PINS_POS )
		(DIFF_PAIR_PINS_NEG )
	)

	(Pin
		(Name SI57X_CLK_P_I)
		(MSB )
		(LSB )
		(Type INPUT)
		(Location Left)
		(InputLoadLow -0.01)
		(InputLoadHigh 0.01)
		(OutputLoadLow )
		(OutputLoadHigh )
		(CheckLoad Both)
		(CheckIO Both)
		(CheckDir 1)
		(CheckAssert 1)
		(CheckOutput 1)
		(UnknownLoading 0)
		(PinShape )
		(DIFF_PAIR_PINS_POS )
		(DIFF_PAIR_PINS_NEG )
	)

	(Pin
		(Name SI57X_OE_O)
		(MSB )
		(LSB )
		(Type OUTPUT)
		(Location Right)
		(InputLoadLow )
		(InputLoadHigh )
		(OutputLoadLow 1.0)
		(OutputLoadHigh -1.0)
		(CheckLoad Both)
		(CheckIO Both)
		(CheckDir 1)
		(CheckAssert 1)
		(CheckOutput 1)
		(UnknownLoading 0)
		(PinShape )
		(DIFF_PAIR_PINS_POS )
		(DIFF_PAIR_PINS_NEG )
	)

	(Pin
		(Name LVDS_LEFT_CLK_N_B)
		(MSB )
		(LSB )
		(Type INPUT)
		(Location Left)
		(InputLoadLow -0.01)
		(InputLoadHigh 0.01)
		(OutputLoadLow )
		(OutputLoadHigh )
		(CheckLoad Off)
		(CheckIO Off)
		(CheckDir 0)
		(CheckAssert 0)
		(CheckOutput 0)
		(UnknownLoading 0)
		(PinShape )
		(DIFF_PAIR_PINS_POS )
		(DIFF_PAIR_PINS_NEG )
	)

	(Pin
		(Name LVDS_LEFT_CLK_P_B)
		(MSB )
		(LSB )
		(Type INPUT)
		(Location Left)
		(InputLoadLow -0.01)
		(InputLoadHigh 0.01)
		(OutputLoadLow )
		(OutputLoadHigh )
		(CheckLoad Both)
		(CheckIO Both)
		(CheckDir 1)
		(CheckAssert 1)
		(CheckOutput 1)
		(UnknownLoading 0)
		(PinShape )
		(DIFF_PAIR_PINS_POS )
		(DIFF_PAIR_PINS_NEG )
	)

	(Pin
		(Name LVDS_RIGHT_CLK_N_B)
		(MSB )
		(LSB )
		(Type INPUT)
		(Location Left)
		(InputLoadLow -0.01)
		(InputLoadHigh 0.01)
		(OutputLoadLow )
		(OutputLoadHigh )
		(CheckLoad Off)
		(CheckIO Off)
		(CheckDir 0)
		(CheckAssert 0)
		(CheckOutput 0)
		(UnknownLoading 0)
		(PinShape )
		(DIFF_PAIR_PINS_POS )
		(DIFF_PAIR_PINS_NEG )
	)

	(Pin
		(Name LVDS_RIGHT_CLK_P_B)
		(MSB )
		(LSB )
		(Type INPUT)
		(Location Left)
		(InputLoadLow -0.01)
		(InputLoadHigh 0.01)
		(OutputLoadLow )
		(OutputLoadHigh )
		(CheckLoad Both)
		(CheckIO Both)
		(CheckDir 1)
		(CheckAssert 1)
		(CheckOutput 1)
		(UnknownLoading 0)
		(PinShape )
		(DIFF_PAIR_PINS_POS )
		(DIFF_PAIR_PINS_NEG )
	)

	(Pin
		(Name LVDS_LEFT_DATA_N_B)
		(MSB 15)
		(LSB 0)
		(Type BIDIR)
		(Location Right)
		(InputLoadLow -0.01)
		(InputLoadHigh 0.01)
		(OutputLoadLow 1.0)
		(OutputLoadHigh -1.0)
		(CheckLoad Both)
		(CheckIO Both)
		(CheckDir 1)
		(CheckAssert 1)
		(CheckOutput 1)
		(UnknownLoading 0)
		(PinShape )
		(DIFF_PAIR_PINS_POS )
		(DIFF_PAIR_PINS_NEG )
	)

	(Pin
		(Name LVDS_LEFT_DATA_P_B)
		(MSB 15)
		(LSB 0)
		(Type OUTPUT)
		(Location Right)
		(InputLoadLow )
		(InputLoadHigh )
		(OutputLoadLow 1.0)
		(OutputLoadHigh -1.0)
		(CheckLoad Both)
		(CheckIO Both)
		(CheckDir 1)
		(CheckAssert 1)
		(CheckOutput 1)
		(UnknownLoading 0)
		(PinShape )
		(DIFF_PAIR_PINS_POS )
		(DIFF_PAIR_PINS_NEG )
	)

	(Pin
		(Name LVDS_RIGHT_DATA_N_B)
		(MSB 15)
		(LSB 0)
		(Type BIDIR)
		(Location Right)
		(InputLoadLow -0.01)
		(InputLoadHigh 0.01)
		(OutputLoadLow 1.0)
		(OutputLoadHigh -1.0)
		(CheckLoad Both)
		(CheckIO Both)
		(CheckDir 1)
		(CheckAssert 1)
		(CheckOutput 1)
		(UnknownLoading 0)
		(PinShape )
		(DIFF_PAIR_PINS_POS )
		(DIFF_PAIR_PINS_NEG )
	)

	(Pin
		(Name LVDS_RIGHT_DATA_P_B)
		(MSB 15)
		(LSB 0)
		(Type OUTPUT)
		(Location Right)
		(InputLoadLow )
		(InputLoadHigh )
		(OutputLoadLow 1.0)
		(OutputLoadHigh -1.0)
		(CheckLoad Both)
		(CheckIO Both)
		(CheckDir 1)
		(CheckAssert 1)
		(CheckOutput 1)
		(UnknownLoading 0)
		(PinShape )
		(DIFF_PAIR_PINS_POS )
		(DIFF_PAIR_PINS_NEG )
	)

	(Pin
		(Name IO_L1N_A24_VREF_1)
		(MSB )
		(LSB )
		(Type POWER)
		(Location Top)
		(InputLoadLow )
		(InputLoadHigh )
		(OutputLoadLow )
		(OutputLoadHigh )
		(CheckLoad Off)
		(CheckIO Off)
		(CheckDir 0)
		(CheckAssert 0)
		(CheckOutput 0)
		(UnknownLoading 0)
		(PinShape )
		(DIFF_PAIR_PINS_POS )
		(DIFF_PAIR_PINS_NEG )
	)

	(Pin
		(Name IO_L1N_VREF_3)
		(MSB )
		(LSB )
		(Type POWER)
		(Location Top)
		(InputLoadLow )
		(InputLoadHigh )
		(OutputLoadLow )
		(OutputLoadHigh )
		(CheckLoad Off)
		(CheckIO Off)
		(CheckDir 0)
		(CheckAssert 0)
		(CheckOutput 0)
		(UnknownLoading 0)
		(PinShape )
		(DIFF_PAIR_PINS_POS )
		(DIFF_PAIR_PINS_NEG )
	)

	(Pin
		(Name IO_L28N_VREF_1)
		(MSB )
		(LSB )
		(Type POWER)
		(Location Top)
		(InputLoadLow )
		(InputLoadHigh )
		(OutputLoadLow )
		(OutputLoadHigh )
		(CheckLoad Off)
		(CheckIO Off)
		(CheckDir 0)
		(CheckAssert 0)
		(CheckOutput 0)
		(UnknownLoading 0)
		(PinShape )
		(DIFF_PAIR_PINS_POS )
		(DIFF_PAIR_PINS_NEG )
	)

	(Pin
		(Name IO_L31N_VREF_3)
		(MSB )
		(LSB )
		(Type POWER)
		(Location Top)
		(InputLoadLow )
		(InputLoadHigh )
		(OutputLoadLow )
		(OutputLoadHigh )
		(CheckLoad Off)
		(CheckIO Off)
		(CheckDir 0)
		(CheckAssert 0)
		(CheckOutput 0)
		(UnknownLoading 0)
		(PinShape )
		(DIFF_PAIR_PINS_POS )
		(DIFF_PAIR_PINS_NEG )
	)

	(Pin
		(Name IO_L53N_VREF_1)
		(MSB )
		(LSB )
		(Type POWER)
		(Location Top)
		(InputLoadLow )
		(InputLoadHigh )
		(OutputLoadLow )
		(OutputLoadHigh )
		(CheckLoad Off)
		(CheckIO Off)
		(CheckDir 0)
		(CheckAssert 0)
		(CheckOutput 0)
		(UnknownLoading 0)
		(PinShape )
		(DIFF_PAIR_PINS_POS )
		(DIFF_PAIR_PINS_NEG )
	)

	(Pin
		(Name IO_L57N_VREF_3)
		(MSB )
		(LSB )
		(Type POWER)
		(Location Top)
		(InputLoadLow )
		(InputLoadHigh )
		(OutputLoadLow )
		(OutputLoadHigh )
		(CheckLoad Off)
		(CheckIO Off)
		(CheckDir 0)
		(CheckAssert 0)
		(CheckOutput 0)
		(UnknownLoading 0)
		(PinShape )
		(DIFF_PAIR_PINS_POS )
		(DIFF_PAIR_PINS_NEG )
	)

	(Pin
		(Name IO_L83N_VREF_3)
		(MSB )
		(LSB )
		(Type POWER)
		(Location Top)
		(InputLoadLow )
		(InputLoadHigh )
		(OutputLoadLow )
		(OutputLoadHigh )
		(CheckLoad Off)
		(CheckIO Off)
		(CheckDir 0)
		(CheckAssert 0)
		(CheckOutput 0)
		(UnknownLoading 0)
		(PinShape )
		(DIFF_PAIR_PINS_POS )
		(DIFF_PAIR_PINS_NEG )
	)

	(Pin
		(Name VBATT)
		(MSB )
		(LSB )
		(Type BIDIR)
		(Location Right)
		(InputLoadLow -0.01)
		(InputLoadHigh 0.01)
		(OutputLoadLow 1.0)
		(OutputLoadHigh -1.0)
		(CheckLoad Both)
		(CheckIO Both)
		(CheckDir 1)
		(CheckAssert 1)
		(CheckOutput 1)
		(UnknownLoading 0)
		(PinShape )
		(DIFF_PAIR_PINS_POS )
		(DIFF_PAIR_PINS_NEG )
	)

	(Pin
		(Name VFS)
		(MSB )
		(LSB )
		(Type BIDIR)
		(Location Right)
		(InputLoadLow -0.01)
		(InputLoadHigh 0.01)
		(OutputLoadLow 1.0)
		(OutputLoadHigh -1.0)
		(CheckLoad Both)
		(CheckIO Both)
		(CheckDir 1)
		(CheckAssert 1)
		(CheckOutput 1)
		(UnknownLoading 0)
		(PinShape )
		(DIFF_PAIR_PINS_POS )
		(DIFF_PAIR_PINS_NEG )
	)

	(Pin
		(Name VCCO_3)
		(MSB 9)
		(LSB 0)
		(Type POWER)
		(Location Top)
		(InputLoadLow )
		(InputLoadHigh )
		(OutputLoadLow )
		(OutputLoadHigh )
		(CheckLoad Off)
		(CheckIO Off)
		(CheckDir 0)
		(CheckAssert 0)
		(CheckOutput 0)
		(UnknownLoading 0)
		(PinShape )
		(DIFF_PAIR_PINS_POS )
		(DIFF_PAIR_PINS_NEG )
	)

	(Pin
		(Name VCCINT)
		(MSB 19)
		(LSB 0)
		(Type POWER)
		(Location Top)
		(InputLoadLow )
		(InputLoadHigh )
		(OutputLoadLow )
		(OutputLoadHigh )
		(CheckLoad Off)
		(CheckIO Off)
		(CheckDir 0)
		(CheckAssert 0)
		(CheckOutput 0)
		(UnknownLoading 0)
		(PinShape )
		(DIFF_PAIR_PINS_POS )
		(DIFF_PAIR_PINS_NEG )
	)

	(Pin
		(Name GND)
		(MSB 70)
		(LSB 0)
		(Type GROUND)
		(Location Top)
		(InputLoadLow )
		(InputLoadHigh )
		(OutputLoadLow )
		(OutputLoadHigh )
		(CheckLoad Off)
		(CheckIO Off)
		(CheckDir 0)
		(CheckAssert 0)
		(CheckOutput 0)
		(UnknownLoading 0)
		(PinShape )
		(DIFF_PAIR_PINS_POS )
		(DIFF_PAIR_PINS_NEG )
	)

	(Pin
		(Name VCCO_0)
		(MSB 5)
		(LSB 0)
		(Type POWER)
		(Location Top)
		(InputLoadLow )
		(InputLoadHigh )
		(OutputLoadLow )
		(OutputLoadHigh )
		(CheckLoad Off)
		(CheckIO Off)
		(CheckDir 0)
		(CheckAssert 0)
		(CheckOutput 0)
		(UnknownLoading 0)
		(PinShape )
		(DIFF_PAIR_PINS_POS )
		(DIFF_PAIR_PINS_NEG )
	)

	(Pin
		(Name VCCO_1)
		(MSB 9)
		(LSB 0)
		(Type POWER)
		(Location Top)
		(InputLoadLow )
		(InputLoadHigh )
		(OutputLoadLow )
		(OutputLoadHigh )
		(CheckLoad Off)
		(CheckIO Off)
		(CheckDir 0)
		(CheckAssert 0)
		(CheckOutput 0)
		(UnknownLoading 0)
		(PinShape )
		(DIFF_PAIR_PINS_POS )
		(DIFF_PAIR_PINS_NEG )
	)

	(Pin
		(Name VCCO_2)
		(MSB 10)
		(LSB 0)
		(Type POWER)
		(Location Top)
		(InputLoadLow )
		(InputLoadHigh )
		(OutputLoadLow )
		(OutputLoadHigh )
		(CheckLoad Off)
		(CheckIO Off)
		(CheckDir 0)
		(CheckAssert 0)
		(CheckOutput 0)
		(UnknownLoading 0)
		(PinShape )
		(DIFF_PAIR_PINS_POS )
		(DIFF_PAIR_PINS_NEG )
	)

	(Pin
		(Name VCCAUX)
		(MSB 12)
		(LSB 0)
		(Type POWER)
		(Location Top)
		(InputLoadLow )
		(InputLoadHigh )
		(OutputLoadLow )
		(OutputLoadHigh )
		(CheckLoad Off)
		(CheckIO Off)
		(CheckDir 0)
		(CheckAssert 0)
		(CheckOutput 0)
		(UnknownLoading 0)
		(PinShape )
		(DIFF_PAIR_PINS_POS )
		(DIFF_PAIR_PINS_NEG )
	)

	(Pin
		(Name ADC_DAV_I)
		(MSB )
		(LSB )
		(Type INPUT)
		(Location Left)
		(InputLoadLow -0.01)
		(InputLoadHigh 0.01)
		(OutputLoadLow )
		(OutputLoadHigh )
		(CheckLoad Both)
		(CheckIO Both)
		(CheckDir 1)
		(CheckAssert 1)
		(CheckOutput 1)
		(UnknownLoading 0)
		(PinShape )
		(DIFF_PAIR_PINS_POS )
		(DIFF_PAIR_PINS_NEG )
	)

	(Pin
		(Name CK_40M_N_O)
		(MSB )
		(LSB )
		(Type OUTPUT)
		(Location Right)
		(InputLoadLow -0.01)
		(InputLoadHigh 0.01)
		(OutputLoadLow 1.0)
		(OutputLoadHigh -1.0)
		(CheckLoad Both)
		(CheckIO Both)
		(CheckDir 1)
		(CheckAssert 1)
		(CheckOutput 1)
		(UnknownLoading 0)
		(PinShape )
		(DIFF_PAIR_PINS_POS )
		(DIFF_PAIR_PINS_NEG )
	)

	(Pin
		(Name CK_40M_P_O)
		(MSB )
		(LSB )
		(Type OUTPUT)
		(Location Right)
		(InputLoadLow )
		(InputLoadHigh )
		(OutputLoadLow 1.0)
		(OutputLoadHigh -1.0)
		(CheckLoad Both)
		(CheckIO Both)
		(CheckDir 1)
		(CheckAssert 1)
		(CheckOutput 1)
		(UnknownLoading 0)
		(PinShape )
		(DIFF_PAIR_PINS_POS )
		(DIFF_PAIR_PINS_NEG )
	)

	(Pin
		(Name CK_R_O)
		(MSB )
		(LSB )
		(Type OUTPUT)
		(Location Right)
		(InputLoadLow )
		(InputLoadHigh )
		(OutputLoadLow 1.0)
		(OutputLoadHigh -1.0)
		(CheckLoad Both)
		(CheckIO Both)
		(CheckDir 1)
		(CheckAssert 1)
		(CheckOutput 1)
		(UnknownLoading 0)
		(PinShape )
		(DIFF_PAIR_PINS_POS )
		(DIFF_PAIR_PINS_NEG )
	)

	(Pin
		(Name CK_SC_O)
		(MSB )
		(LSB )
		(Type OUTPUT)
		(Location Right)
		(InputLoadLow )
		(InputLoadHigh )
		(OutputLoadLow 1.0)
		(OutputLoadHigh -1.0)
		(CheckLoad Both)
		(CheckIO Both)
		(CheckDir 1)
		(CheckAssert 1)
		(CheckOutput 1)
		(UnknownLoading 0)
		(PinShape )
		(DIFF_PAIR_PINS_POS )
		(DIFF_PAIR_PINS_NEG )
	)

	(Pin
		(Name D_R_O)
		(MSB )
		(LSB )
		(Type OUTPUT)
		(Location Right)
		(InputLoadLow )
		(InputLoadHigh )
		(OutputLoadLow 1.0)
		(OutputLoadHigh -1.0)
		(CheckLoad Both)
		(CheckIO Both)
		(CheckDir 1)
		(CheckAssert 1)
		(CheckOutput 1)
		(UnknownLoading 0)
		(PinShape )
		(DIFF_PAIR_PINS_POS )
		(DIFF_PAIR_PINS_NEG )
	)

	(Pin
		(Name D_SC_O)
		(MSB )
		(LSB )
		(Type OUTPUT)
		(Location Right)
		(InputLoadLow )
		(InputLoadHigh )
		(OutputLoadLow 1.0)
		(OutputLoadHigh -1.0)
		(CheckLoad Both)
		(CheckIO Both)
		(CheckDir 1)
		(CheckAssert 1)
		(CheckOutput 1)
		(UnknownLoading 0)
		(PinShape )
		(DIFF_PAIR_PINS_POS )
		(DIFF_PAIR_PINS_NEG )
	)

	(Pin
		(Name EN_OTAQ_O)
		(MSB )
		(LSB )
		(Type OUTPUT)
		(Location Right)
		(InputLoadLow )
		(InputLoadHigh )
		(OutputLoadLow 1.0)
		(OutputLoadHigh -1.0)
		(CheckLoad Both)
		(CheckIO Both)
		(CheckDir 1)
		(CheckAssert 1)
		(CheckOutput 1)
		(UnknownLoading 0)
		(PinShape )
		(DIFF_PAIR_PINS_POS )
		(DIFF_PAIR_PINS_NEG )
	)

	(Pin
		(Name HOLD1_O)
		(MSB )
		(LSB )
		(Type OUTPUT)
		(Location Right)
		(InputLoadLow )
		(InputLoadHigh )
		(OutputLoadLow 1.0)
		(OutputLoadHigh -1.0)
		(CheckLoad Both)
		(CheckIO Both)
		(CheckDir 1)
		(CheckAssert 1)
		(CheckOutput 1)
		(UnknownLoading 0)
		(PinShape )
		(DIFF_PAIR_PINS_POS )
		(DIFF_PAIR_PINS_NEG )
	)

	(Pin
		(Name HOLD2_O)
		(MSB )
		(LSB )
		(Type OUTPUT)
		(Location Right)
		(InputLoadLow )
		(InputLoadHigh )
		(OutputLoadLow 1.0)
		(OutputLoadHigh -1.0)
		(CheckLoad Both)
		(CheckIO Both)
		(CheckDir 1)
		(CheckAssert 1)
		(CheckOutput 1)
		(UnknownLoading 0)
		(PinShape )
		(DIFF_PAIR_PINS_POS )
		(DIFF_PAIR_PINS_NEG )
	)

	(Pin
		(Name OUT_ADC_I)
		(MSB )
		(LSB )
		(Type INPUT)
		(Location Left)
		(InputLoadLow -0.01)
		(InputLoadHigh 0.01)
		(OutputLoadLow )
		(OutputLoadHigh )
		(CheckLoad Both)
		(CheckIO Both)
		(CheckDir 1)
		(CheckAssert 1)
		(CheckOutput 1)
		(UnknownLoading 0)
		(PinShape )
		(DIFF_PAIR_PINS_POS )
		(DIFF_PAIR_PINS_NEG )
	)

	(Pin
		(Name Q_R_I)
		(MSB )
		(LSB )
		(Type INPUT)
		(Location Left)
		(InputLoadLow -0.01)
		(InputLoadHigh 0.01)
		(OutputLoadLow )
		(OutputLoadHigh )
		(CheckLoad Both)
		(CheckIO Both)
		(CheckDir 1)
		(CheckAssert 1)
		(CheckOutput 1)
		(UnknownLoading 0)
		(PinShape )
		(DIFF_PAIR_PINS_POS )
		(DIFF_PAIR_PINS_NEG )
	)

	(Pin
		(Name Q_SC_I)
		(MSB )
		(LSB )
		(Type INPUT)
		(Location Left)
		(InputLoadLow -0.01)
		(InputLoadHigh 0.01)
		(OutputLoadLow )
		(OutputLoadHigh )
		(CheckLoad Both)
		(CheckIO Both)
		(CheckDir 1)
		(CheckAssert 1)
		(CheckOutput 1)
		(UnknownLoading 0)
		(PinShape )
		(DIFF_PAIR_PINS_POS )
		(DIFF_PAIR_PINS_NEG )
	)

	(Pin
		(Name RST_ADC_N_O)
		(MSB )
		(LSB )
		(Type OUTPUT)
		(Location Right)
		(InputLoadLow )
		(InputLoadHigh )
		(OutputLoadLow 1.0)
		(OutputLoadHigh -1.0)
		(CheckLoad Both)
		(CheckIO Both)
		(CheckDir 1)
		(CheckAssert 1)
		(CheckOutput 1)
		(UnknownLoading 0)
		(PinShape )
		(DIFF_PAIR_PINS_POS )
		(DIFF_PAIR_PINS_NEG )
	)

	(Pin
		(Name RST_R_N_O)
		(MSB )
		(LSB )
		(Type OUTPUT)
		(Location Right)
		(InputLoadLow )
		(InputLoadHigh )
		(OutputLoadLow 1.0)
		(OutputLoadHigh -1.0)
		(CheckLoad Both)
		(CheckIO Both)
		(CheckDir 1)
		(CheckAssert 1)
		(CheckOutput 1)
		(UnknownLoading 0)
		(PinShape )
		(DIFF_PAIR_PINS_POS )
		(DIFF_PAIR_PINS_NEG )
	)

	(Pin
		(Name RST_SC_N_O)
		(MSB )
		(LSB )
		(Type OUTPUT)
		(Location Right)
		(InputLoadLow )
		(InputLoadHigh )
		(OutputLoadLow 1.0)
		(OutputLoadHigh -1.0)
		(CheckLoad Both)
		(CheckIO Both)
		(CheckDir 1)
		(CheckAssert 1)
		(CheckOutput 1)
		(UnknownLoading 0)
		(PinShape )
		(DIFF_PAIR_PINS_POS )
		(DIFF_PAIR_PINS_NEG )
	)

	(Pin
		(Name START_ADC_N_O)
		(MSB )
		(LSB )
		(Type OUTPUT)
		(Location Right)
		(InputLoadLow )
		(InputLoadHigh )
		(OutputLoadLow 1.0)
		(OutputLoadHigh -1.0)
		(CheckLoad Both)
		(CheckIO Both)
		(CheckDir 1)
		(CheckAssert 1)
		(CheckOutput 1)
		(UnknownLoading 0)
		(PinShape )
		(DIFF_PAIR_PINS_POS )
		(DIFF_PAIR_PINS_NEG )
	)

	(Pin
		(Name MAROC_TRIGGER_I)
		(MSB 63)
		(LSB 0)
		(Type INPUT)
		(Location Left)
		(InputLoadLow -0.01)
		(InputLoadHigh 0.01)
		(OutputLoadLow )
		(OutputLoadHigh )
		(CheckLoad Both)
		(CheckIO Both)
		(CheckDir 1)
		(CheckAssert 1)
		(CheckOutput 1)
		(UnknownLoading 0)
		(PinShape )
		(DIFF_PAIR_PINS_POS )
		(DIFF_PAIR_PINS_NEG )
	)

	(Pin
		(Name OR_I)
		(MSB 1)
		(LSB 0)
		(Type INPUT)
		(Location Left)
		(InputLoadLow -0.01)
		(InputLoadHigh 0.01)
		(OutputLoadLow )
		(OutputLoadHigh )
		(CheckLoad Both)
		(CheckIO Both)
		(CheckDir 1)
		(CheckAssert 1)
		(CheckOutput 1)
		(UnknownLoading 0)
		(PinShape )
		(DIFF_PAIR_PINS_POS )
		(DIFF_PAIR_PINS_NEG )
	)

	(Pin
		(Name FPGA_PLL_REF_CLK_101_N_I)
		(MSB )
		(LSB )
		(Type INPUT)
		(Location Left)
		(InputLoadLow -0.01)
		(InputLoadHigh 0.01)
		(OutputLoadLow )
		(OutputLoadHigh )
		(CheckLoad Both)
		(CheckIO Both)
		(CheckDir 1)
		(CheckAssert 1)
		(CheckOutput 1)
		(UnknownLoading 0)
		(PinShape )
		(DIFF_PAIR_PINS_POS )
		(DIFF_PAIR_PINS_NEG )
	)

	(Pin
		(Name FPGA_PLL_REF_CLK_101_P_I)
		(MSB )
		(LSB )
		(Type INPUT)
		(Location Left)
		(InputLoadLow -0.01)
		(InputLoadHigh 0.01)
		(OutputLoadLow )
		(OutputLoadHigh )
		(CheckLoad Both)
		(CheckIO Both)
		(CheckDir 1)
		(CheckAssert 1)
		(CheckOutput 1)
		(UnknownLoading 0)
		(PinShape )
		(DIFF_PAIR_PINS_POS )
		(DIFF_PAIR_PINS_NEG )
	)

	(Pin
		(Name FPGA_PLL_REF_CLK_123_N_I)
		(MSB )
		(LSB )
		(Type INPUT)
		(Location Left)
		(InputLoadLow -0.01)
		(InputLoadHigh 0.01)
		(OutputLoadLow )
		(OutputLoadHigh )
		(CheckLoad Both)
		(CheckIO Both)
		(CheckDir 1)
		(CheckAssert 1)
		(CheckOutput 1)
		(UnknownLoading 0)
		(PinShape )
		(DIFF_PAIR_PINS_POS )
		(DIFF_PAIR_PINS_NEG )
	)

	(Pin
		(Name FPGA_PLL_REF_CLK_123_P_I)
		(MSB )
		(LSB )
		(Type INPUT)
		(Location Left)
		(InputLoadLow -0.01)
		(InputLoadHigh 0.01)
		(OutputLoadLow )
		(OutputLoadHigh )
		(CheckLoad Both)
		(CheckIO Both)
		(CheckDir 1)
		(CheckAssert 1)
		(CheckOutput 1)
		(UnknownLoading 0)
		(PinShape )
		(DIFF_PAIR_PINS_POS )
		(DIFF_PAIR_PINS_NEG )
	)

	(Pin
		(Name MGTAVCCPLL0_101)
		(MSB )
		(LSB )
		(Type BIDIR)
		(Location Right)
		(InputLoadLow -0.01)
		(InputLoadHigh 0.01)
		(OutputLoadLow 1.0)
		(OutputLoadHigh -1.0)
		(CheckLoad Both)
		(CheckIO Both)
		(CheckDir 1)
		(CheckAssert 1)
		(CheckOutput 1)
		(UnknownLoading 0)
		(PinShape )
		(DIFF_PAIR_PINS_POS )
		(DIFF_PAIR_PINS_NEG )
	)

	(Pin
		(Name MGTAVCCPLL0_123)
		(MSB )
		(LSB )
		(Type BIDIR)
		(Location Right)
		(InputLoadLow -0.01)
		(InputLoadHigh 0.01)
		(OutputLoadLow 1.0)
		(OutputLoadHigh -1.0)
		(CheckLoad Both)
		(CheckIO Both)
		(CheckDir 1)
		(CheckAssert 1)
		(CheckOutput 1)
		(UnknownLoading 0)
		(PinShape )
		(DIFF_PAIR_PINS_POS )
		(DIFF_PAIR_PINS_NEG )
	)

	(Pin
		(Name MGTAVCCPLL1_101)
		(MSB )
		(LSB )
		(Type BIDIR)
		(Location Right)
		(InputLoadLow -0.01)
		(InputLoadHigh 0.01)
		(OutputLoadLow 1.0)
		(OutputLoadHigh -1.0)
		(CheckLoad Both)
		(CheckIO Both)
		(CheckDir 1)
		(CheckAssert 1)
		(CheckOutput 1)
		(UnknownLoading 0)
		(PinShape )
		(DIFF_PAIR_PINS_POS )
		(DIFF_PAIR_PINS_NEG )
	)

	(Pin
		(Name MGTAVCCPLL1_123)
		(MSB )
		(LSB )
		(Type BIDIR)
		(Location Right)
		(InputLoadLow -0.01)
		(InputLoadHigh 0.01)
		(OutputLoadLow 1.0)
		(OutputLoadHigh -1.0)
		(CheckLoad Both)
		(CheckIO Both)
		(CheckDir 1)
		(CheckAssert 1)
		(CheckOutput 1)
		(UnknownLoading 0)
		(PinShape )
		(DIFF_PAIR_PINS_POS )
		(DIFF_PAIR_PINS_NEG )
	)

	(Pin
		(Name MGTAVCC_101)
		(MSB )
		(LSB )
		(Type BIDIR)
		(Location Right)
		(InputLoadLow -0.01)
		(InputLoadHigh 0.01)
		(OutputLoadLow 1.0)
		(OutputLoadHigh -1.0)
		(CheckLoad Both)
		(CheckIO Both)
		(CheckDir 1)
		(CheckAssert 1)
		(CheckOutput 1)
		(UnknownLoading 0)
		(PinShape )
		(DIFF_PAIR_PINS_POS )
		(DIFF_PAIR_PINS_NEG )
	)

	(Pin
		(Name MGTAVCC_123)
		(MSB )
		(LSB )
		(Type BIDIR)
		(Location Right)
		(InputLoadLow -0.01)
		(InputLoadHigh 0.01)
		(OutputLoadLow 1.0)
		(OutputLoadHigh -1.0)
		(CheckLoad Both)
		(CheckIO Both)
		(CheckDir 1)
		(CheckAssert 1)
		(CheckOutput 1)
		(UnknownLoading 0)
		(PinShape )
		(DIFF_PAIR_PINS_POS )
		(DIFF_PAIR_PINS_NEG )
	)

	(Pin
		(Name MGTAVTTRCAL_101)
		(MSB )
		(LSB )
		(Type BIDIR)
		(Location Right)
		(InputLoadLow -0.01)
		(InputLoadHigh 0.01)
		(OutputLoadLow 1.0)
		(OutputLoadHigh -1.0)
		(CheckLoad Both)
		(CheckIO Both)
		(CheckDir 1)
		(CheckAssert 1)
		(CheckOutput 1)
		(UnknownLoading 0)
		(PinShape )
		(DIFF_PAIR_PINS_POS )
		(DIFF_PAIR_PINS_NEG )
	)

	(Pin
		(Name MGTAVTTRX_101)
		(MSB )
		(LSB )
		(Type BIDIR)
		(Location Right)
		(InputLoadLow -0.01)
		(InputLoadHigh 0.01)
		(OutputLoadLow 1.0)
		(OutputLoadHigh -1.0)
		(CheckLoad Both)
		(CheckIO Both)
		(CheckDir 1)
		(CheckAssert 1)
		(CheckOutput 1)
		(UnknownLoading 0)
		(PinShape )
		(DIFF_PAIR_PINS_POS )
		(DIFF_PAIR_PINS_NEG )
	)

	(Pin
		(Name MGTAVTTRX_123)
		(MSB )
		(LSB )
		(Type BIDIR)
		(Location Right)
		(InputLoadLow -0.01)
		(InputLoadHigh 0.01)
		(OutputLoadLow 1.0)
		(OutputLoadHigh -1.0)
		(CheckLoad Both)
		(CheckIO Both)
		(CheckDir 1)
		(CheckAssert 1)
		(CheckOutput 1)
		(UnknownLoading 0)
		(PinShape )
		(DIFF_PAIR_PINS_POS )
		(DIFF_PAIR_PINS_NEG )
	)

	(Pin
		(Name MGTAVTTTX_101)
		(MSB )
		(LSB )
		(Type BIDIR)
		(Location Right)
		(InputLoadLow -0.01)
		(InputLoadHigh 0.01)
		(OutputLoadLow 1.0)
		(OutputLoadHigh -1.0)
		(CheckLoad Both)
		(CheckIO Both)
		(CheckDir 1)
		(CheckAssert 1)
		(CheckOutput 1)
		(UnknownLoading 0)
		(PinShape )
		(DIFF_PAIR_PINS_POS )
		(DIFF_PAIR_PINS_NEG )
	)

	(Pin
		(Name MGTAVTTTX_123)
		(MSB )
		(LSB )
		(Type BIDIR)
		(Location Right)
		(InputLoadLow -0.01)
		(InputLoadHigh 0.01)
		(OutputLoadLow 1.0)
		(OutputLoadHigh -1.0)
		(CheckLoad Both)
		(CheckIO Both)
		(CheckDir 1)
		(CheckAssert 1)
		(CheckOutput 1)
		(UnknownLoading 0)
		(PinShape )
		(DIFF_PAIR_PINS_POS )
		(DIFF_PAIR_PINS_NEG )
	)

	(Pin
		(Name MGTRREF_101)
		(MSB )
		(LSB )
		(Type BIDIR)
		(Location Right)
		(InputLoadLow -0.01)
		(InputLoadHigh 0.01)
		(OutputLoadLow 1.0)
		(OutputLoadHigh -1.0)
		(CheckLoad Both)
		(CheckIO Both)
		(CheckDir 1)
		(CheckAssert 1)
		(CheckOutput 1)
		(UnknownLoading 0)
		(PinShape )
		(DIFF_PAIR_PINS_POS )
		(DIFF_PAIR_PINS_NEG )
	)

	(Pin
		(Name SATA_RXN_I)
		(MSB 1)
		(LSB 0)
		(Type INPUT)
		(Location Left)
		(InputLoadLow -0.01)
		(InputLoadHigh 0.01)
		(OutputLoadLow )
		(OutputLoadHigh )
		(CheckLoad Both)
		(CheckIO Both)
		(CheckDir 1)
		(CheckAssert 1)
		(CheckOutput 1)
		(UnknownLoading 0)
		(PinShape )
		(DIFF_PAIR_PINS_POS )
		(DIFF_PAIR_PINS_NEG )
	)

	(Pin
		(Name SFP_TXN_O)
		(MSB 1)
		(LSB 0)
		(Type OUTPUT)
		(Location Right)
		(InputLoadLow )
		(InputLoadHigh )
		(OutputLoadLow 1.0)
		(OutputLoadHigh -1.0)
		(CheckLoad Both)
		(CheckIO Both)
		(CheckDir 1)
		(CheckAssert 1)
		(CheckOutput 1)
		(UnknownLoading 0)
		(PinShape )
		(DIFF_PAIR_PINS_POS )
		(DIFF_PAIR_PINS_NEG )
	)

	(Pin
		(Name SFP_LOS_I)
		(MSB 1)
		(LSB 0)
		(Type INPUT)
		(Location Left)
		(InputLoadLow -0.01)
		(InputLoadHigh 0.01)
		(OutputLoadLow )
		(OutputLoadHigh )
		(CheckLoad Both)
		(CheckIO Both)
		(CheckDir 1)
		(CheckAssert 1)
		(CheckOutput 1)
		(UnknownLoading 0)
		(PinShape )
		(DIFF_PAIR_PINS_POS )
		(DIFF_PAIR_PINS_NEG )
	)

	(Pin
		(Name SATA_RXP_I)
		(MSB 1)
		(LSB 0)
		(Type INPUT)
		(Location Left)
		(InputLoadLow -0.01)
		(InputLoadHigh 0.01)
		(OutputLoadLow )
		(OutputLoadHigh )
		(CheckLoad Both)
		(CheckIO Both)
		(CheckDir 1)
		(CheckAssert 1)
		(CheckOutput 1)
		(UnknownLoading 0)
		(PinShape )
		(DIFF_PAIR_PINS_POS )
		(DIFF_PAIR_PINS_NEG )
	)

	(Pin
		(Name SFP_TXP_O)
		(MSB 1)
		(LSB 0)
		(Type OUTPUT)
		(Location Right)
		(InputLoadLow )
		(InputLoadHigh )
		(OutputLoadLow 1.0)
		(OutputLoadHigh -1.0)
		(CheckLoad Both)
		(CheckIO Both)
		(CheckDir 1)
		(CheckAssert 1)
		(CheckOutput 1)
		(UnknownLoading 0)
		(PinShape )
		(DIFF_PAIR_PINS_POS )
		(DIFF_PAIR_PINS_NEG )
	)

	(Pin
		(Name SFP_TX_DISABLE_O)
		(MSB 1)
		(LSB 0)
		(Type OUTPUT)
		(Location Right)
		(InputLoadLow )
		(InputLoadHigh )
		(OutputLoadLow 1.0)
		(OutputLoadHigh -1.0)
		(CheckLoad Both)
		(CheckIO Both)
		(CheckDir 1)
		(CheckAssert 1)
		(CheckOutput 1)
		(UnknownLoading 0)
		(PinShape )
		(DIFF_PAIR_PINS_POS )
		(DIFF_PAIR_PINS_NEG )
	)

	(Pin
		(Name SFP_RATE_SELECT_B)
		(MSB 1)
		(LSB 0)
		(Type OUTPUT)
		(Location Right)
		(InputLoadLow )
		(InputLoadHigh )
		(OutputLoadLow 1.0)
		(OutputLoadHigh -1.0)
		(CheckLoad Both)
		(CheckIO Both)
		(CheckDir 1)
		(CheckAssert 1)
		(CheckOutput 1)
		(UnknownLoading 0)
		(PinShape )
		(DIFF_PAIR_PINS_POS )
		(DIFF_PAIR_PINS_NEG )
	)

	(Pin
		(Name SATA_TXN_O)
		(MSB 1)
		(LSB 0)
		(Type OUTPUT)
		(Location Right)
		(InputLoadLow )
		(InputLoadHigh )
		(OutputLoadLow 1.0)
		(OutputLoadHigh -1.0)
		(CheckLoad Both)
		(CheckIO Both)
		(CheckDir 1)
		(CheckAssert 1)
		(CheckOutput 1)
		(UnknownLoading 0)
		(PinShape )
		(DIFF_PAIR_PINS_POS )
		(DIFF_PAIR_PINS_NEG )
	)

	(Pin
		(Name SFP_RXN_I)
		(MSB 1)
		(LSB 0)
		(Type INPUT)
		(Location Left)
		(InputLoadLow -0.01)
		(InputLoadHigh 0.01)
		(OutputLoadLow )
		(OutputLoadHigh )
		(CheckLoad Both)
		(CheckIO Both)
		(CheckDir 1)
		(CheckAssert 1)
		(CheckOutput 1)
		(UnknownLoading 0)
		(PinShape )
		(DIFF_PAIR_PINS_POS )
		(DIFF_PAIR_PINS_NEG )
	)

	(Pin
		(Name SFP_MOD_DEF0_B)
		(MSB 1)
		(LSB 0)
		(Type OUTPUT)
		(Location Left)
		(InputLoadLow -0.01)
		(InputLoadHigh 0.01)
		(OutputLoadLow 1.0)
		(OutputLoadHigh -1.0)
		(CheckLoad Both)
		(CheckIO Both)
		(CheckDir 1)
		(CheckAssert 1)
		(CheckOutput 1)
		(UnknownLoading 0)
		(PinShape )
		(DIFF_PAIR_PINS_POS )
		(DIFF_PAIR_PINS_NEG )
	)

	(Pin
		(Name SATA_TXP_O)
		(MSB 1)
		(LSB 0)
		(Type OUTPUT)
		(Location Right)
		(InputLoadLow )
		(InputLoadHigh )
		(OutputLoadLow 1.0)
		(OutputLoadHigh -1.0)
		(CheckLoad Both)
		(CheckIO Both)
		(CheckDir 1)
		(CheckAssert 1)
		(CheckOutput 1)
		(UnknownLoading 0)
		(PinShape )
		(DIFF_PAIR_PINS_POS )
		(DIFF_PAIR_PINS_NEG )
	)

	(Pin
		(Name SFP_MOD_DEF1_B)
		(MSB 1)
		(LSB 0)
		(Type OUTPUT)
		(Location Right)
		(InputLoadLow -0.01)
		(InputLoadHigh 0.01)
		(OutputLoadLow 1.0)
		(OutputLoadHigh -1.0)
		(CheckLoad Both)
		(CheckIO Both)
		(CheckDir 1)
		(CheckAssert 1)
		(CheckOutput 1)
		(UnknownLoading 0)
		(PinShape )
		(DIFF_PAIR_PINS_POS )
		(DIFF_PAIR_PINS_NEG )
	)

	(Pin
		(Name SFP_TX_FAULT_I)
		(MSB 1)
		(LSB 0)
		(Type INPUT)
		(Location Left)
		(InputLoadLow -0.01)
		(InputLoadHigh 0.01)
		(OutputLoadLow )
		(OutputLoadHigh )
		(CheckLoad Both)
		(CheckIO Both)
		(CheckDir 1)
		(CheckAssert 1)
		(CheckOutput 1)
		(UnknownLoading 0)
		(PinShape )
		(DIFF_PAIR_PINS_POS )
		(DIFF_PAIR_PINS_NEG )
	)

	(Pin
		(Name SFP_RXP_I)
		(MSB 1)
		(LSB 0)
		(Type INPUT)
		(Location Left)
		(InputLoadLow -0.01)
		(InputLoadHigh 0.01)
		(OutputLoadLow )
		(OutputLoadHigh )
		(CheckLoad Both)
		(CheckIO Both)
		(CheckDir 1)
		(CheckAssert 1)
		(CheckOutput 1)
		(UnknownLoading 0)
		(PinShape )
		(DIFF_PAIR_PINS_POS )
		(DIFF_PAIR_PINS_NEG )
	)

	(Pin
		(Name SFP_MOD_DEF2_B)
		(MSB 1)
		(LSB 0)
		(Type OUTPUT)
		(Location Right)
		(InputLoadLow -0.01)
		(InputLoadHigh 0.01)
		(OutputLoadLow 1.0)
		(OutputLoadHigh -1.0)
		(CheckLoad Both)
		(CheckIO Both)
		(CheckDir 1)
		(CheckAssert 1)
		(CheckOutput 1)
		(UnknownLoading 0)
		(PinShape )
		(DIFF_PAIR_PINS_POS )
		(DIFF_PAIR_PINS_NEG )
	)

	(Pin
		(Name CMPCS_B_2)
		(MSB )
		(LSB )
		(Type BIDIR)
		(Location Right)
		(InputLoadLow -0.01)
		(InputLoadHigh 0.01)
		(OutputLoadLow 1.0)
		(OutputLoadHigh -1.0)
		(CheckLoad Both)
		(CheckIO Both)
		(CheckDir 1)
		(CheckAssert 1)
		(CheckOutput 1)
		(UnknownLoading 0)
		(PinShape Line)
		(DIFF_PAIR_PINS_POS )
		(DIFF_PAIR_PINS_NEG )
	)

	(Pin
		(Name DONE_2)
		(MSB )
		(LSB )
		(Type BIDIR)
		(Location Right)
		(InputLoadLow -0.01)
		(InputLoadHigh 0.01)
		(OutputLoadLow 1.0)
		(OutputLoadHigh -1.0)
		(CheckLoad Both)
		(CheckIO Both)
		(CheckDir 1)
		(CheckAssert 1)
		(CheckOutput 1)
		(UnknownLoading 0)
		(PinShape Line)
		(DIFF_PAIR_PINS_POS )
		(DIFF_PAIR_PINS_NEG )
	)

	(Pin
		(Name PROGRAM_B_2)
		(MSB )
		(LSB )
		(Type BIDIR)
		(Location Right)
		(InputLoadLow -0.01)
		(InputLoadHigh 0.01)
		(OutputLoadLow 1.0)
		(OutputLoadHigh -1.0)
		(CheckLoad Both)
		(CheckIO Both)
		(CheckDir 1)
		(CheckAssert 1)
		(CheckOutput 1)
		(UnknownLoading 0)
		(PinShape Line)
		(DIFF_PAIR_PINS_POS )
		(DIFF_PAIR_PINS_NEG )
	)

	(Pin
		(Name RFUSE)
		(MSB )
		(LSB )
		(Type BIDIR)
		(Location Right)
		(InputLoadLow -0.01)
		(InputLoadHigh 0.01)
		(OutputLoadLow 1.0)
		(OutputLoadHigh -1.0)
		(CheckLoad Both)
		(CheckIO Both)
		(CheckDir 1)
		(CheckAssert 1)
		(CheckOutput 1)
		(UnknownLoading 0)
		(PinShape Line)
		(DIFF_PAIR_PINS_POS )
		(DIFF_PAIR_PINS_NEG )
	)

	(Pin
		(Name SUSPEND)
		(MSB )
		(LSB )
		(Type BIDIR)
		(Location Right)
		(InputLoadLow -0.01)
		(InputLoadHigh 0.01)
		(OutputLoadLow 1.0)
		(OutputLoadHigh -1.0)
		(CheckLoad Both)
		(CheckIO Both)
		(CheckDir 1)
		(CheckAssert 1)
		(CheckOutput 1)
		(UnknownLoading 0)
		(PinShape Line)
		(DIFF_PAIR_PINS_POS )
		(DIFF_PAIR_PINS_NEG )
	)

	(Pin
		(Name TCK)
		(MSB )
		(LSB )
		(Type INPUT)
		(Location Right)
		(InputLoadLow -0.01)
		(InputLoadHigh 0.01)
		(OutputLoadLow 1.0)
		(OutputLoadHigh -1.0)
		(CheckLoad Both)
		(CheckIO Both)
		(CheckDir 1)
		(CheckAssert 1)
		(CheckOutput 1)
		(UnknownLoading 0)
		(PinShape Line)
		(DIFF_PAIR_PINS_POS )
		(DIFF_PAIR_PINS_NEG )
	)

	(Pin
		(Name TDI)
		(MSB )
		(LSB )
		(Type INPUT)
		(Location Right)
		(InputLoadLow -0.01)
		(InputLoadHigh 0.01)
		(OutputLoadLow 1.0)
		(OutputLoadHigh -1.0)
		(CheckLoad Both)
		(CheckIO Both)
		(CheckDir 1)
		(CheckAssert 1)
		(CheckOutput 1)
		(UnknownLoading 0)
		(PinShape Line)
		(DIFF_PAIR_PINS_POS )
		(DIFF_PAIR_PINS_NEG )
	)

	(Pin
		(Name TDO)
		(MSB )
		(LSB )
		(Type OUTPUT)
		(Location Right)
		(InputLoadLow -0.01)
		(InputLoadHigh 0.01)
		(OutputLoadLow 1.0)
		(OutputLoadHigh -1.0)
		(CheckLoad Both)
		(CheckIO Both)
		(CheckDir 1)
		(CheckAssert 1)
		(CheckOutput 1)
		(UnknownLoading 0)
		(PinShape Line)
		(DIFF_PAIR_PINS_POS )
		(DIFF_PAIR_PINS_NEG )
	)

	(Pin
		(Name TMS)
		(MSB )
		(LSB )
		(Type INPUT)
		(Location Right)
		(InputLoadLow -0.01)
		(InputLoadHigh 0.01)
		(OutputLoadLow 1.0)
		(OutputLoadHigh -1.0)
		(CheckLoad Both)
		(CheckIO Both)
		(CheckDir 1)
		(CheckAssert 1)
		(CheckOutput 1)
		(UnknownLoading 0)
		(PinShape Line)
		(DIFF_PAIR_PINS_POS )
		(DIFF_PAIR_PINS_NEG )
	)

	(Pin
		(Name M0)
		(MSB )
		(LSB )
		(Type INPUT)
		(Location Left)
		(InputLoadLow -0.01)
		(InputLoadHigh 0.01)
		(OutputLoadLow )
		(OutputLoadHigh )
		(CheckLoad Both)
		(CheckIO Both)
		(CheckDir 1)
		(CheckAssert 1)
		(CheckOutput 1)
		(UnknownLoading 0)
		(PinShape Line)
		(DIFF_PAIR_PINS_POS )
		(DIFF_PAIR_PINS_NEG )
	)

	(Pin
		(Name M1)
		(MSB )
		(LSB )
		(Type INPUT)
		(Location Left)
		(InputLoadLow -0.01)
		(InputLoadHigh 0.01)
		(OutputLoadLow )
		(OutputLoadHigh )
		(CheckLoad Both)
		(CheckIO Both)
		(CheckDir 1)
		(CheckAssert 1)
		(CheckOutput 1)
		(UnknownLoading 0)
		(PinShape Line)
		(DIFF_PAIR_PINS_POS )
		(DIFF_PAIR_PINS_NEG )
	)

	(Pin
		(Name CSO_B)
		(MSB )
		(LSB )
		(Type BIDIR)
		(Location Right)
		(InputLoadLow -0.01)
		(InputLoadHigh 0.01)
		(OutputLoadLow 1.0)
		(OutputLoadHigh -1.0)
		(CheckLoad Both)
		(CheckIO Both)
		(CheckDir 1)
		(CheckAssert 1)
		(CheckOutput 1)
		(UnknownLoading 0)
		(PinShape Line)
		(DIFF_PAIR_PINS_POS )
		(DIFF_PAIR_PINS_NEG )
	)

	(Pin
		(Name DIN)
		(MSB )
		(LSB )
		(Type INPUT)
		(Location Left)
		(InputLoadLow -0.01)
		(InputLoadHigh 0.01)
		(OutputLoadLow )
		(OutputLoadHigh )
		(CheckLoad Both)
		(CheckIO Both)
		(CheckDir 1)
		(CheckAssert 1)
		(CheckOutput 1)
		(UnknownLoading 0)
		(PinShape Line)
		(DIFF_PAIR_PINS_POS )
		(DIFF_PAIR_PINS_NEG )
	)

	(Pin
		(Name MOSI)
		(MSB )
		(LSB )
		(Type OUTPUT)
		(Location Right)
		(InputLoadLow )
		(InputLoadHigh )
		(OutputLoadLow 1.0)
		(OutputLoadHigh -1.0)
		(CheckLoad Both)
		(CheckIO Both)
		(CheckDir 1)
		(CheckAssert 1)
		(CheckOutput 1)
		(UnknownLoading 0)
		(PinShape Line)
		(DIFF_PAIR_PINS_POS )
		(DIFF_PAIR_PINS_NEG )
	)

	(Pin
		(Name CCLK)
		(MSB )
		(LSB )
		(Type OUTPUT)
		(Location Right)
		(InputLoadLow )
		(InputLoadHigh )
		(OutputLoadLow 1.0)
		(OutputLoadHigh -1.0)
		(CheckLoad Both)
		(CheckIO Both)
		(CheckDir 1)
		(CheckAssert 1)
		(CheckOutput 1)
		(UnknownLoading 0)
		(PinShape Line)
		(DIFF_PAIR_PINS_POS )
		(DIFF_PAIR_PINS_NEG )
	)

	(Pin
		(Name INIT_B)
		(MSB )
		(LSB )
		(Type INPUT)
		(Location Left)
		(InputLoadLow -0.01)
		(InputLoadHigh 0.01)
		(OutputLoadLow )
		(OutputLoadHigh )
		(CheckLoad Both)
		(CheckIO Both)
		(CheckDir 1)
		(CheckAssert 1)
		(CheckOutput 1)
		(UnknownLoading 0)
		(PinShape Line)
		(DIFF_PAIR_PINS_POS )
		(DIFF_PAIR_PINS_NEG )
	)

)

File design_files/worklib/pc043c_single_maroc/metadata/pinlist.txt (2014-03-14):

(Pinlist
	(Pin
		(Name TRIG)
		(MSB 63)
		(LSB 0)
		(Type UNSPEC)
		(Location Right)
		(InputLoadLow )
		(InputLoadHigh )
		(OutputLoadLow )
		(OutputLoadHigh )
		(CheckLoad Off)
		(CheckIO Off)
		(CheckDir 0)
		(CheckAssert 0)
		(CheckOutput 0)
		(UnknownLoading 0)
		(PinShape Line)
		(DIFF_PAIR_PINS_POS )
		(DIFF_PAIR_PINS_NEG )
	)

	(Pin
		(Name SUM)
		(MSB 8)
		(LSB 1)
		(Type UNSPEC)
		(Location Right)
		(InputLoadLow )
		(InputLoadHigh )
		(OutputLoadLow )
		(OutputLoadHigh )
		(CheckLoad Off)
		(CheckIO Off)
		(CheckDir 0)
		(CheckAssert 0)
		(CheckOutput 0)
		(UnknownLoading 0)
		(PinShape Line)
		(DIFF_PAIR_PINS_POS )
		(DIFF_PAIR_PINS_NEG )
	)

	(Pin
		(Name QBUF_SC)
		(MSB )
		(LSB )
		(Type UNSPEC)
		(Location Right)
		(InputLoadLow )
		(InputLoadHigh )
		(OutputLoadLow )
		(OutputLoadHigh )
		(CheckLoad Off)
		(CheckIO Off)
		(CheckDir 0)
		(CheckAssert 0)
		(CheckOutput 0)
		(UnknownLoading 0)
		(PinShape Line)
		(DIFF_PAIR_PINS_POS )
		(DIFF_PAIR_PINS_NEG )
	)

	(Pin
		(Name QBUF_R)
		(MSB )
		(LSB )
		(Type UNSPEC)
		(Location Right)
		(InputLoadLow )
		(InputLoadHigh )
		(OutputLoadLow )
		(OutputLoadHigh )
		(CheckLoad Off)
		(CheckIO Off)
		(CheckDir 0)
		(CheckAssert 0)
		(CheckOutput 0)
		(UnknownLoading 0)
		(PinShape Line)
		(DIFF_PAIR_PINS_POS )
		(DIFF_PAIR_PINS_NEG )
	)

	(Pin
		(Name OUT_ADC)
		(MSB )
		(LSB )
		(Type UNSPEC)
		(Location Right)
		(InputLoadLow )
		(InputLoadHigh )
		(OutputLoadLow )
		(OutputLoadHigh )
		(CheckLoad Off)
		(CheckIO Off)
		(CheckDir 0)
		(CheckAssert 0)
		(CheckOutput 0)
		(UnknownLoading 0)
		(PinShape Line)
		(DIFF_PAIR_PINS_POS )
		(DIFF_PAIR_PINS_NEG )
	)

	(Pin
		(Name OR)
		(MSB 1)
		(LSB 0)
		(Type UNSPEC)
		(Location Right)
		(InputLoadLow )
		(InputLoadHigh )
		(OutputLoadLow )
		(OutputLoadHigh )
		(CheckLoad Off)
		(CheckIO Off)
		(CheckDir 0)
		(CheckAssert 0)
		(CheckOutput 0)
		(UnknownLoading 0)
		(PinShape Line)
		(DIFF_PAIR_PINS_POS )
		(DIFF_PAIR_PINS_NEG )
	)

	(Pin
		(Name BUF_OUT_Q)
		(MSB )
		(LSB )
		(Type UNSPEC)
		(Location Right)
		(InputLoadLow )
		(InputLoadHigh )
		(OutputLoadLow )
		(OutputLoadHigh )
		(CheckLoad Off)
		(CheckIO Off)
		(CheckDir 0)
		(CheckAssert 0)
		(CheckOutput 0)
		(UnknownLoading 0)
		(PinShape Line)
		(DIFF_PAIR_PINS_POS )
		(DIFF_PAIR_PINS_NEG )
	)

	(Pin
		(Name BUF_OUT_FS)
		(MSB )
		(LSB )
		(Type UNSPEC)
		(Location Right)
		(InputLoadLow )
		(InputLoadHigh )
		(OutputLoadLow )
		(OutputLoadHigh )
		(CheckLoad Off)
		(CheckIO Off)
		(CheckDir 0)
		(CheckAssert 0)
		(CheckOutput 0)
		(UnknownLoading 0)
		(PinShape Line)
		(DIFF_PAIR_PINS_POS )
		(DIFF_PAIR_PINS_NEG )
	)

	(Pin
		(Name ADC_DAV)
		(MSB )
		(LSB )
		(Type UNSPEC)
		(Location Right)
		(InputLoadLow )
		(InputLoadHigh )
		(OutputLoadLow )
		(OutputLoadHigh )
		(CheckLoad Off)
		(CheckIO Off)
		(CheckDir 0)
		(CheckAssert 0)
		(CheckOutput 0)
		(UnknownLoading 0)
		(PinShape Line)
		(DIFF_PAIR_PINS_POS )
		(DIFF_PAIR_PINS_NEG )
	)

	(Pin
		(Name VL)
		(MSB )
		(LSB )
		(Type UNSPEC)
		(Location Left)
		(InputLoadLow )
		(InputLoadHigh )
		(OutputLoadLow )
		(OutputLoadHigh )
		(CheckLoad Off)
		(CheckIO Off)
		(CheckDir 0)
		(CheckAssert 0)
		(CheckOutput 0)
		(UnknownLoading 0)
		(PinShape Line)
		(DIFF_PAIR_PINS_POS )
		(DIFF_PAIR_PINS_NEG )
	)

	(Pin
		(Name VH)
		(MSB )
		(LSB )
		(Type UNSPEC)
		(Location Left)
		(InputLoadLow )
		(InputLoadHigh )
		(OutputLoadLow )
		(OutputLoadHigh )
		(CheckLoad Off)
		(CheckIO Off)
		(CheckDir 0)
		(CheckAssert 0)
		(CheckOutput 0)
		(UnknownLoading 0)
		(PinShape Line)
		(DIFF_PAIR_PINS_POS )
		(DIFF_PAIR_PINS_NEG )
	)

	(Pin
		(Name START_ADCB)
		(MSB )
		(LSB )
		(Type UNSPEC)
		(Location Left)
		(InputLoadLow )
		(InputLoadHigh )
		(OutputLoadLow )
		(OutputLoadHigh )
		(CheckLoad Off)
		(CheckIO Off)
		(CheckDir 0)
		(CheckAssert 0)
		(CheckOutput 0)
		(UnknownLoading 0)
		(PinShape Line)
		(DIFF_PAIR_PINS_POS )
		(DIFF_PAIR_PINS_NEG )
	)

	(Pin
		(Name RSTN_SC)
		(MSB )
		(LSB )
		(Type UNSPEC)
		(Location Left)
		(InputLoadLow )
		(InputLoadHigh )
		(OutputLoadLow )
		(OutputLoadHigh )
		(CheckLoad Off)
		(CheckIO Off)
		(CheckDir 0)
		(CheckAssert 0)
		(CheckOutput 0)
		(UnknownLoading 0)
		(PinShape Line)
		(DIFF_PAIR_PINS_POS )
		(DIFF_PAIR_PINS_NEG )
	)

	(Pin
		(Name RSTN_ADC)
		(MSB )
		(LSB )
		(Type UNSPEC)
		(Location Left)
		(InputLoadLow )
		(InputLoadHigh )
		(OutputLoadLow )
		(OutputLoadHigh )
		(CheckLoad Off)
		(CheckIO Off)
		(CheckDir 0)
		(CheckAssert 0)
		(CheckOutput 0)
		(UnknownLoading 0)
		(PinShape Line)
		(DIFF_PAIR_PINS_POS )
		(DIFF_PAIR_PINS_NEG )
	)

	(Pin
		(Name RSTB_R)
		(MSB )
		(LSB )
		(Type UNSPEC)
		(Location Left)
		(InputLoadLow )
		(InputLoadHigh )
		(OutputLoadLow )
		(OutputLoadHigh )
		(CheckLoad Off)
		(CheckIO Off)
		(CheckDir 0)
		(CheckAssert 0)
		(CheckOutput 0)
		(UnknownLoading 0)
		(PinShape Line)
		(DIFF_PAIR_PINS_POS )
		(DIFF_PAIR_PINS_NEG )
	)

	(Pin
		(Name HOLD2)
		(MSB )
		(LSB )
		(Type UNSPEC)
		(Location Left)
		(InputLoadLow )
		(InputLoadHigh )
		(OutputLoadLow )
		(OutputLoadHigh )
		(CheckLoad Off)
		(CheckIO Off)
		(CheckDir 0)
		(CheckAssert 0)
		(CheckOutput 0)
		(UnknownLoading 0)
		(PinShape Line)
		(DIFF_PAIR_PINS_POS )
		(DIFF_PAIR_PINS_NEG )
	)

	(Pin
		(Name HOLD1)
		(MSB )
		(LSB )
		(Type UNSPEC)
		(Location Left)
		(InputLoadLow )
		(InputLoadHigh )
		(OutputLoadLow )
		(OutputLoadHigh )
		(CheckLoad Off)
		(CheckIO Off)
		(CheckDir 0)
		(CheckAssert 0)
		(CheckOutput 0)
		(UnknownLoading 0)
		(PinShape Line)
		(DIFF_PAIR_PINS_POS )
		(DIFF_PAIR_PINS_NEG )
	)

	(Pin
		(Name EN_OTAG)
		(MSB )
		(LSB )
		(Type UNSPEC)
		(Location Left)
		(InputLoadLow )
		(InputLoadHigh )
		(OutputLoadLow )
		(OutputLoadHigh )
		(CheckLoad Off)
		(CheckIO Off)
		(CheckDir 0)
		(CheckAssert 0)
		(CheckOutput 0)
		(UnknownLoading 0)
		(PinShape Line)
		(DIFF_PAIR_PINS_POS )
		(DIFF_PAIR_PINS_NEG )
	)

	(Pin
		(Name D_SC)
		(MSB )
		(LSB )
		(Type UNSPEC)
		(Location Left)
		(InputLoadLow )
		(InputLoadHigh )
		(OutputLoadLow )
		(OutputLoadHigh )
		(CheckLoad Off)
		(CheckIO Off)
		(CheckDir 0)
		(CheckAssert 0)
		(CheckOutput 0)
		(UnknownLoading 0)
		(PinShape Line)
		(DIFF_PAIR_PINS_POS )
		(DIFF_PAIR_PINS_NEG )
	)

	(Pin
		(Name D_R)
		(MSB )
		(LSB )
		(Type UNSPEC)
		(Location Left)
		(InputLoadLow )
		(InputLoadHigh )
		(OutputLoadLow )
		(OutputLoadHigh )
		(CheckLoad Off)
		(CheckIO Off)
		(CheckDir 0)
		(CheckAssert 0)
		(CheckOutput 0)
		(UnknownLoading 0)
		(PinShape Line)
		(DIFF_PAIR_PINS_POS )
		(DIFF_PAIR_PINS_NEG )
	)

	(Pin
		(Name CTEST)
		(MSB )
		(LSB )
		(Type UNSPEC)
		(Location Left)
		(InputLoadLow )
		(InputLoadHigh )
		(OutputLoadLow )
		(OutputLoadHigh )
		(CheckLoad Off)
		(CheckIO Off)
		(CheckDir 0)
		(CheckAssert 0)
		(CheckOutput 0)
		(UnknownLoading 0)
		(PinShape Line)
		(DIFF_PAIR_PINS_POS )
		(DIFF_PAIR_PINS_NEG )
	)

	(Pin
		(Name CK_SC)
		(MSB )
		(LSB )
		(Type UNSPEC)
		(Location Left)
		(InputLoadLow )
		(InputLoadHigh )
		(OutputLoadLow )
		(OutputLoadHigh )
		(CheckLoad Off)
		(CheckIO Off)
		(CheckDir 0)
		(CheckAssert 0)
		(CheckOutput 0)
		(UnknownLoading 0)
		(PinShape Line)
		(DIFF_PAIR_PINS_POS )
		(DIFF_PAIR_PINS_NEG )
	)

	(Pin
		(Name CK_R)
		(MSB )
		(LSB )
		(Type UNSPEC)
		(Location Left)
		(InputLoadLow )
		(InputLoadHigh )
		(OutputLoadLow )
		(OutputLoadHigh )
		(CheckLoad Off)
		(CheckIO Off)
		(CheckDir 0)
		(CheckAssert 0)
		(CheckOutput 0)
		(UnknownLoading 0)
		(PinShape Line)
		(DIFF_PAIR_PINS_POS )
		(DIFF_PAIR_PINS_NEG )
	)

	(Pin
		(Name CK_40M)
		(MSB )
		(LSB )
		(Type UNSPEC)
		(Location Left)
		(InputLoadLow )
		(InputLoadHigh )
		(OutputLoadLow )
		(OutputLoadHigh )
		(CheckLoad Off)
		(CheckIO Off)
		(CheckDir 0)
		(CheckAssert 0)
		(CheckOutput 0)
		(UnknownLoading 0)
		(PinShape Line)
		(DIFF_PAIR_PINS_POS )
		(DIFF_PAIR_PINS_NEG )
	)

	(Pin
		(Name CKB_40M)
		(MSB )
		(LSB )
		(Type UNSPEC)
		(Location Left)
		(InputLoadLow )
		(InputLoadHigh )
		(OutputLoadLow )
		(OutputLoadHigh )
		(CheckLoad Off)
		(CheckIO Off)
		(CheckDir 0)
		(CheckAssert 0)
		(CheckOutput 0)
		(UnknownLoading 0)
		(PinShape Line)
		(DIFF_PAIR_PINS_POS )
		(DIFF_PAIR_PINS_NEG )
	)

)

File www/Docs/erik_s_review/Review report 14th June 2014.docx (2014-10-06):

14th June 2014

Review report for UOB_HEP_PC049A_lib

Reviewer: Erik Schooneveld

## Introduction

I will discuss the issues that I would like to flag per schematic page. I have divided the issues that I would like to flag into 4 categories:

1) Issues that definitely need attention and possibly modification. These are marked in red.
2) Issues where I am certainly worried about, but that will not necessarily result in a malfunctioning of the board. If you have implemented the same circuit in one of your earlier boards, we might ignore those issues after a discussion. These are marked in magenta.
3) Warning or issues that I would have differently; but I cannot “proof” that my way is better. It also be an issue that I just have a question about. These issues are marked in blue.
4) Issues that could make the board neater, such as using slightly different components that are easier to buy. These are marked in green.

I don’t have Acrobat, so I cannot edit the .pdf file and colour code the issues that I have found. Hence you will have to cross-correlate the Word and .pdf files. I will highlight the text in text in the .pdf file (without colour coding), making it easier for you to spot my issues

## Page 2

ADC_DAV: There is (probably) an error in the pin assignment of the MAROC chip in your design, see my discussion on Page 14. Depending on how you rectify the pin assignment error, you might have to update the assignment on Page 2.

OUT_ADC: MAROC pin assignment issue, see Page 14; same as for ADC_DAV.

START_ADCB: From what I can see from the MAROC datasheet, I get the impression that the Omega guys use the letter b (B in your schematic) to indicate inverted/negative logic signal; sometimes they use n. Hence I would read START_ADCB is an active low signal. In versions V7 and V8 of the MAROC data sheet Omega calls the signal “start_ADC”, implying that the signal is active high. Hence the naming of your START_ADCB doesn’t comply with the MAROC naming of the signal and might incorrectly suggest that it signal is active low. The MAROC datasheet V7 indicates that at some stage the name of the signal has been change, which could explain the discrepancy between your naming and the naming in the new datasheets. Please let me know if the signal is indeed active low in which case you can forget my issue.

RSTN_ADC: As with START_ADCB, the naming doesn’t comply with the MAROC datasheet and might incorrectly suggests an active low signal.

QTS-075-03-F-D-A: This connector is only available through Samtec; I do have ordered components directly from Samtec without any problem. You can only buy 500+ from Farnell for the QTS-075-03-F-D-A, which is unattractive, but the QTS-075-02-F-D-A (and QTS-075-02-L-D-A) are available from Farnell in small quantities; the -02- versions are slightly lower profile/height (8mm high when mated versus 11mm high for -03- version). The -02- is also a fair bit cheaper, but that isn’t an issue for me. Do you prefer the higher versions? I can imagine that the -03- version is your standard, so I am happy to use the -03- version. By the way, the L-D-A version has a 0.25 µm thick gold plating instead of 0.075 µm for the –F-D-A version that you specified (>3 times thicker) for virtually the same price (£2 more expensive) ; 0.075 µm gold is very thin. I assume that the –L-D-A- therefore can withstand more mating cycles. I would therefore prefer the QTS-075-03-L-D-A version over the QTS-075-03-F-D-A.

## Page 3

J2: A28, J2: A29, J3: A4 and J3: A5 (P3V3 pins): I have the impression that if you daisy-chain multiple boards that (for example) pin J2:A29 of one board will mate with pin J3: A4 of the other board. This will cause the P3V3 of the two boards to be shorted/linked together. I assume that you want to be able to daisy-chain multiple boards but don’t want to short the 3V3 supplies of different boards; I wouldn’t like to do that.

Pretty much all pins of the connectors are used, so it isn’t easy to reserve more pins for the 3V3 power supply. I assume that you have made the 3V3 connections especially for us/ISIS and that you don’t need them. Harting specifies a 2A current rating for the pins. I cannot imagine that one of our daughter boards will use more than 2A, so we will not need more than one pin. Hence the solution could be to use pin J2: A28 for 3V3 and leave pin J2: A29 disconnected. For J3 we could leave pin J3: A5 disconnected and use pin J3:A4 for 3V3. This way the 3V3 power supplies of daisy-chained boards will not be shorted (at the cost of having a factor of two lower current for our daughter boards).

P12V: Current rating. If the power dissipation per board is really ~60W (as the rating of the regulators suggest), you will not able to daisy-chain multiple boards and distribute the 12V over the DIN connectors. However, I cannot imagine that the power dissipation of a board is really 60 W, probably not more than 10W, so in practice the current rating of the 12V line isn’t a problem.

## Page 4

MLVDS_GLOBALTRIG and MLVDS_GCLK: Termination. I cannot see a 100 Ohm termination anywhere on these lines and I know that (normal) LVDS outputs need a termination because they are current outputs. To be honest, I don’t know whether B-LVDS are current outputs, like true normal LVDS. Anyway, it might be idea to put a 100 Ohm do not fit (DNF) resistor somewhere on the line so that we can terminate the signal lines.

IC8: I agree that the common-mode voltage of LVDS is outside the specs of the MC100EP05DG. Although a bit slower, the MC100LVEL05 is a safer bet.

IC8: Did you intend to make this into an and-gate (for coincidence) instead of an or-gate? It is easy to get polarities the wrong way round.

C1, C2, C4-C8: Package and value. Is it advantageous to use an 0603 package? They are easily available in 0402 package, higher speed and for decoupling capacitors I doubt that the large size has lay-out advantages. 100nF capacitors don’t look like high frequency components to me. Both ECL and LVDS have no low frequency power current and signal current components, so large value is not needed from that point of view. I would have used ~10nF, but couldn’t find a good datasheet to proof that 10nF is definitely higher speed than 100nF.

I50: Does a Spartan 6 FPGAs have dedicated clock inputs? From the documentation I got the impression that this is not the case, but I am not sure; Altera FPGAs do have dedicated clock inputs.

DS90LV001TM and DS92001TMA: These contain lead. The DS90LV001TM/NOPB and DS92001TMA/NOPB don’t contain lead and are easier to buy.

## Page 5

Sorry, I flag a lot of issues here, but clocks are in my opinion very important, so better safe than sorry.

PLL25DAC_SCLK, PLL25DAC_DIN, PLL25DAC1_SYNC_N and PLL25DAC2_SYNC_N: Pull-up resistors. Are these I2C logic type signals? I cannot see this because that is defined by FPGA. If they are I2C, they will need pull-up resistors.

IC11 and R24: Output type. I assume that the output type of the clock buffer will be set to LVDS. CMOS could/will give problems because the CLK_125M_PLLREF signals go to FPGA pins with a VCCO of 2.5V. They would also need proper termination if they are CMOS. If the output type of the CDCM61004 is meant to be LVDS, R24 should be a do not fit (DNF).

R18 and R22: DNF. I assume that you want a 125MHz output frequency. According to the documentation, to get 125MhHz out, PR0 and PR1 should both be high. This means a DNF for both resistors.

R19 and R23: DNF. I assume that you want a 125MHz output frequency. According to the documentation, to get 125MhHz out, OD0 and OD1 should both be high. This means a DNF for both R19 and R23.

SFP_CLK_P and SFP_CLK_N: Termination. If IC11 is set to LVDS output type and the CDCM61004 has true LVDS (current source) outputs, these outputs/signals need to be terminated with 100 Ohm even if they are not used.

CLK_125M_PLLREF_P and CLK_125M_PLLREF_N: Problem if output of IC11 is set to CMOS (see above).

QZ2, IC1 and IC9: I don’t see dedicated/own power supply bypass capacitors for these chips.

L5 and L6: Current rating. If these are ferrites with 220 Ohm impedance, the current rating of these beads is too low; 150mA rating and >= 150mA current dissipation. The marking/name suggests that you want to use a 22Ohm ferrite, which probably would have had a sufficient current rating, but Vishay doesn’t make 22 Ohm beads; hence I assumed these are 220 Ohm beads. For a higher current rating 220 Ohm beads, you could use the Laird LI0603G221R-10 (Farnell 2292434); this is the same manufacturer of the other type of bead that you use in the design.

U1: Is U1 close to IC11? The output of U1 is an unterminated clock line.

SI57X_CLK_P and SI57X_CLK_N: Termination. Is the SI570 (QZ1) very close to the FPGA? The clock signals are not terminated, so the quality of the clock might get worse if the distance is too large. Silicon Labs use a 10 Ohm series resistors for the CMOS outputs on their evaluation board.

C59: The Si570 evaluation board has 33uF tantalum and 1uF (and 100nF) ceramic capacitors for the power supply bypassing.

C51: Low voltage rating.

C52-C55: Voltage rating. A 4V rating of these capacitors is on the low side for a 3.3V power supply. I probably would have gone for an 0805 package or even better replace the two 22 uF caps with a 10uF ceramic 0603 in parallel with a 33uF tantalum B-size capacitor.

C65 and C67: Voltage rating. TI doesn’t specify the voltage on the REG_CAP pins, so it could be up to 3V. A 4V rating of these capacitors is therefore on the low side; remember that the capacitance drops with applied voltage. I would therefore have chosen for 10uF, 6.3V capacitor; 10uF is the minimum/recommended value of TI.

C71: This is a 10 uF capacitor on TI evaluation board. This might be compensated for by the 22uF capacitor is the P3V3A filter.

QZ1: I2C address. The Si web sites gives that the Si570 has I2C address hex 55, or binary 0101 0101

LM4040CIM3-2.5: This is not a lead free part. The LM4040CIM3-2.5/NOPB is lead free.

## Page 6

This is a whole list, but that shows that I am unfamiliar with transceivers.

SATA_SRX_N, SATA_SRX_P, SATA_STX_N and SATA_STX_P: Pin connection problem/inversion. As I mentioned in my E-mail, I think that in the schematic and netlist of 4th June these signals are connected to the MGT pins with the inverse polarity. For example the SATA_SRX_N signal (inverted signal) is connected to FPGA pin D13, MGTRXP0_123, which is as far as I understand the positive/ non-inverted input of MGTRX0_123. The same is true for the other SATA slave signals.

Pins F12, E12, D11 and C11: Pin numbering incorrect. According to the Spartan 6 Pinouts user guide (UG385), pin F12 is the MGTREFCLK1N_123 input whereas it is marked as FPGA_PLL_REF_CLK_101_N_I (signal FPGA_PLL_REF_CLK101_N) in your schematic. The same is true for the other pins. Hence I think that you have swapped F12 with D11 and E12 with C11.

SFPx_MOD_DEF, SFPx_TX_FAULT and SFPx_LOS: Pull-up resistor. Manufacturers suggest to pull these signals with 4K7 to 10K resistors to VCC (3V3) as the SFP modules have open drain outputs; the MOD_DEF[1..2] signals are I2C signals. Does the Spartan 6 have a programmable pull-up resistor for the pins that are used on the FPGA? For Altera FPGAs not all pins have pull-up resistors. If the Spartan 6 doesn’t have pull-up resistors for these pins, we need external resistors.

J4 and J5: Molex doesn’t make this particular SATA connector anymore. Neither Farnell, RS, Mouser nor DigiKey sells those anymore. I don’t know of a suitable replacement, as I don’t know whether you have specific wishes.

FPGA_PLL_REF_CLK_101 and FPGA_PLL_REF_CLK_123: AC-coupling. According to the “GTP Reference Clock Checklist” in UG386, the GTPA1_DUAL clock input pins should be AC coupled. On page 170 they give an example of how to couple LVDS signals with the clock inputs. Unfortunately this example doesn’t show a 100 termination resistor before the capacitors so that we have a problem with the current if the CDCM61004 has true (current) LVDS outputs.

SFP_RXN<1..0>, SFP_RXP<1..0>, SFP_TXN<1..0> and SFP_TXP<1..0>: AC-decoupling. Do the SFP units have their own AC-decoupling capacitors for these signals? These lines don’t have capacitors, whereas the SATA lines do, and I guess that the Spartan 6 prefers AC-coupled signals.

C104-C114: These capacitors do not conform the Recommended Minimum Decoupling values in UG386, page 173. UG386 recommends two 4.7uF and eight 220nF capacitors.

C14-C21: Do both the TX and RX channels need AC-coupling capacitors? If we use the SATA connectors purely for inter-board communication (hard linked), than there is a minor issue that the DC voltage level of the signal between the Tx and Rx is not defined. I guess that strictly speaking only the (for example) Rx lines need a capacitor, as long as we use the SATA connectors purely for inter-board communication. Not sure what is required if you use the SATA signal lines for communication with for example computers. I am happy to leave the capacitors for both the Tx and Rx lines (as you did).

C14-C21: 100nF looks like a high value for ~100MHz signals, so I am worried about high frequency behaviour. For SATA 3G and 6G, 10nF is a more widely used value. Again, I have no datasheets showing the real impedance of 10nF and 100nF capacitors, so you can leave them as 100nF if you are happy with them.

C13, C23, C28 and C30: The same old (boring) story of the voltage rating.

## Page 7

IC16: The chip doesn’t seem to have its own power supply bypass capacitor.

SPI_CCLK: Mmm, I think that the 100 Ohm // 100 Ohm termination is a bit risky. According to UG380 the CClk output is 8mA. With a 50 Ohm parallel termination, this means that the voltage swing is 400mV (50 * 8mA). This is outside the specs of the S25FL128SAGMFIR0. Serial termination doesn’t have this disadvantage. However, this is the clock termination scheme that Xilinx recommends, so I (a bit reluctantly) agree with the implementation. We definitely have to pull CCLK low or high (not high impedance) after configuration.

SW4: The OMRON documentation shows another pin numbering, but you have probably tailored the PCB pad numbering to the pin numbering of the schematic so that the layout is OK.

IC22: The 128MB is just 1% too small to store the uncompressed firmware for a XC6SLX150T, my preferred FPGA. Still I am happy with the 128MB, as I don’t envisage to use 99% of the logic and compression will reduce the required memory probably enough to fit in the flash memory.

I56 (Spartan 6): HSWAPEN. I don’t see HSWAPEN pulled down anywhere on the schematic, unlike Fig 2-12 in UG380 where it is pulled low. This means that the outputs of the FPGA will in high impedance state during programming, instead of being pulled up; Altera FPGAs pull the outputs high during configuration. I think that a high impedance is OK for most outputs, but I am not sure whether the MAROC gets upset when some of its (digital) inputs are floating.

## Page 8

RN1 and RN2: Why such a high resistance, as it (probably) will be too high for impedance matching?

LD2 and LD5: Realize that for the HSMH-C150, the dot mark on the diode is indicating the anode whereas it is the cathode for the other LEDs. Does it make sense to change to pin numbering of the LEDs so that the dot is always pin 2 (or pin 1)?

C3: 0603 package. Like C1, and many more capacitors, I am not sure that it will be advantageous to use an 0603 package instead of the 0402 that you use for other components. See the file “pc049a_summary_Erik.xls” for more components where there are multiple components used for the same value/ package, such as X7R vs X5R or the voltage rating.

RZ1: Is obsolete/unavailable. I suggest the TC164-JR-07150, which is also used for RN1 and RN2.

RZ2: Is obsolete/unavailable. I suggest the TC164-JR-07150.

J10: Only available directly from Samtec.
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

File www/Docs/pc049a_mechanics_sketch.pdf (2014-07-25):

Aluminium
Mounting

Lemo connectors
( 8 x 8 array,

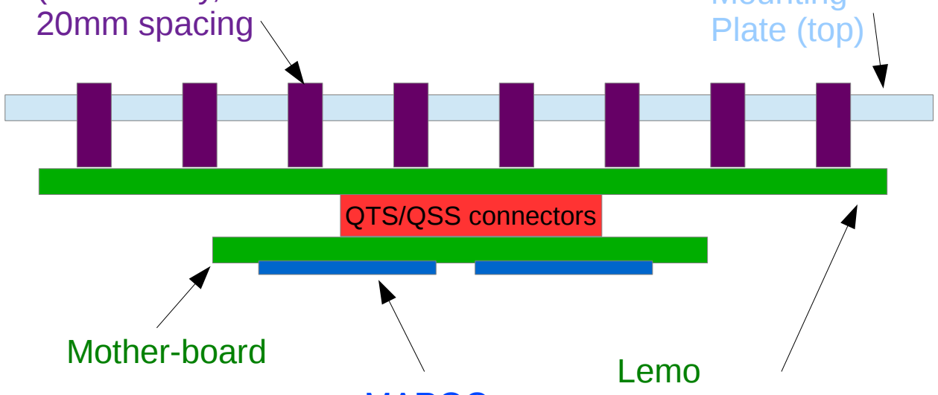
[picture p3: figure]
QTS/QSS connectors; Plate (top); 20mm spacing; Lemo; Mother-board

daughter-board

MAROC,
FPGA, SFP
etc.

Aluminium
Mounting
Plate (top)

N.B. Pillars holding components together not shown.

Drawing not to scale.

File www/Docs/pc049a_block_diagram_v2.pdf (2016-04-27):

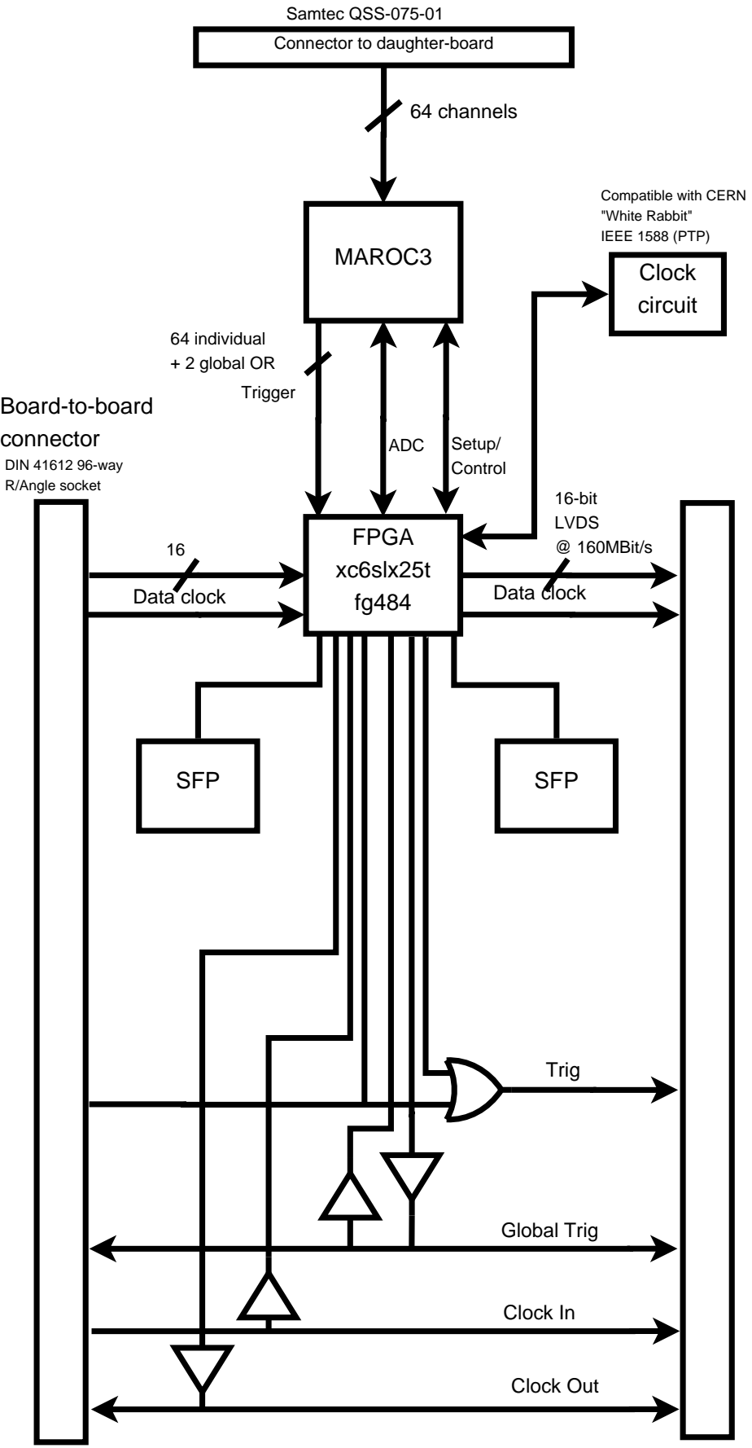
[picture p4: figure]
Connector to daughter-board; 64 channels; MAROC3; FPGA xc6slx25t fg484; Setup/ Control; ADC; Trigger; 64 individual + 2 global OR; Board-to-board connector; 16-bit LVDS @ 160MBit/s; Trig; Global Trig; Clock In; Clock Out; Clock circuit; DIN 41612 96-way R/Angle socket; Samtec QSS-075-01; Data clock; Compatible with CERN "White Rabbit" IEEE 1588 (PTP); SFP

## Board-to-board connector

DIN 41612 96-way
R/Angle plug

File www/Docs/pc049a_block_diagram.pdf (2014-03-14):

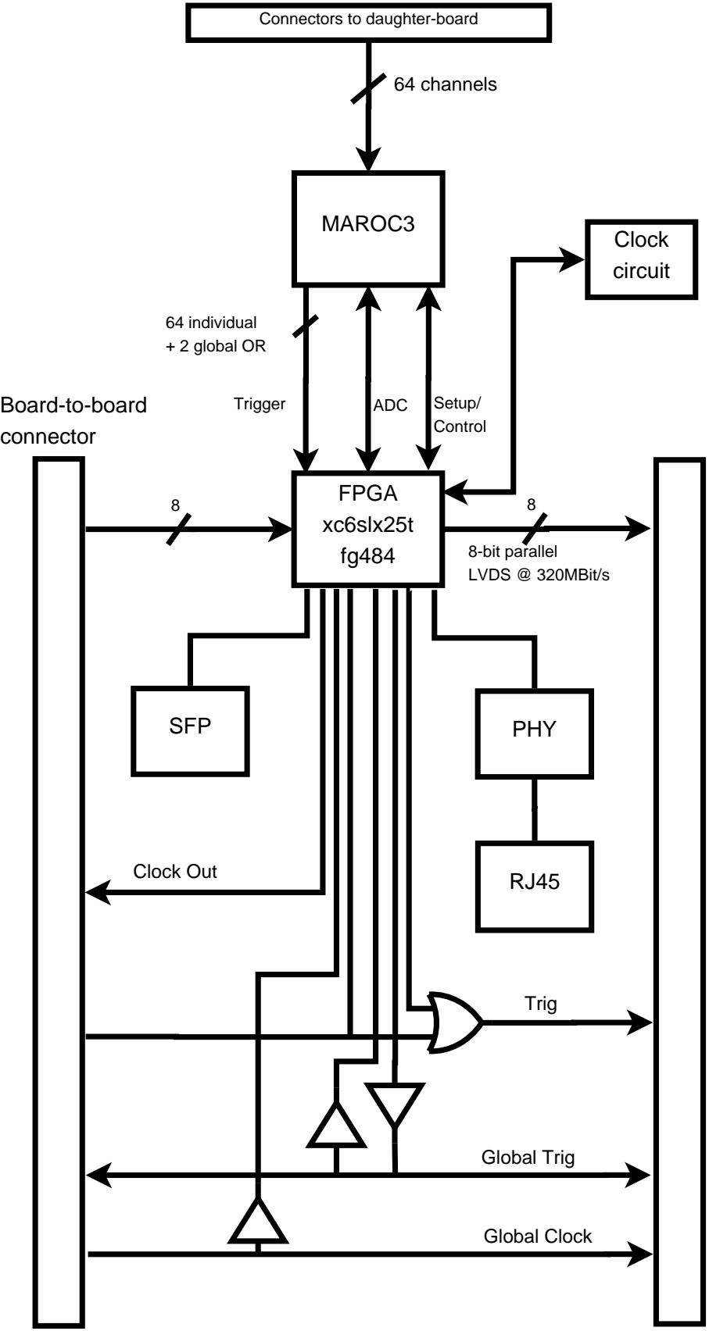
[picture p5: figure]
Connectors to daughter-board; 64 channels; MAROC3; FPGA xc6slx25t fg484; Setup/ Control; Trigger; ADC; 64 individual + 2 global OR; SFP; PHY; Board-to-board connector; 8-bit parallel LVDS @ 320MBit/s; Trig; Global Trig; Global Clock; Clock Out; Clock circuit

## Board-to-board connector

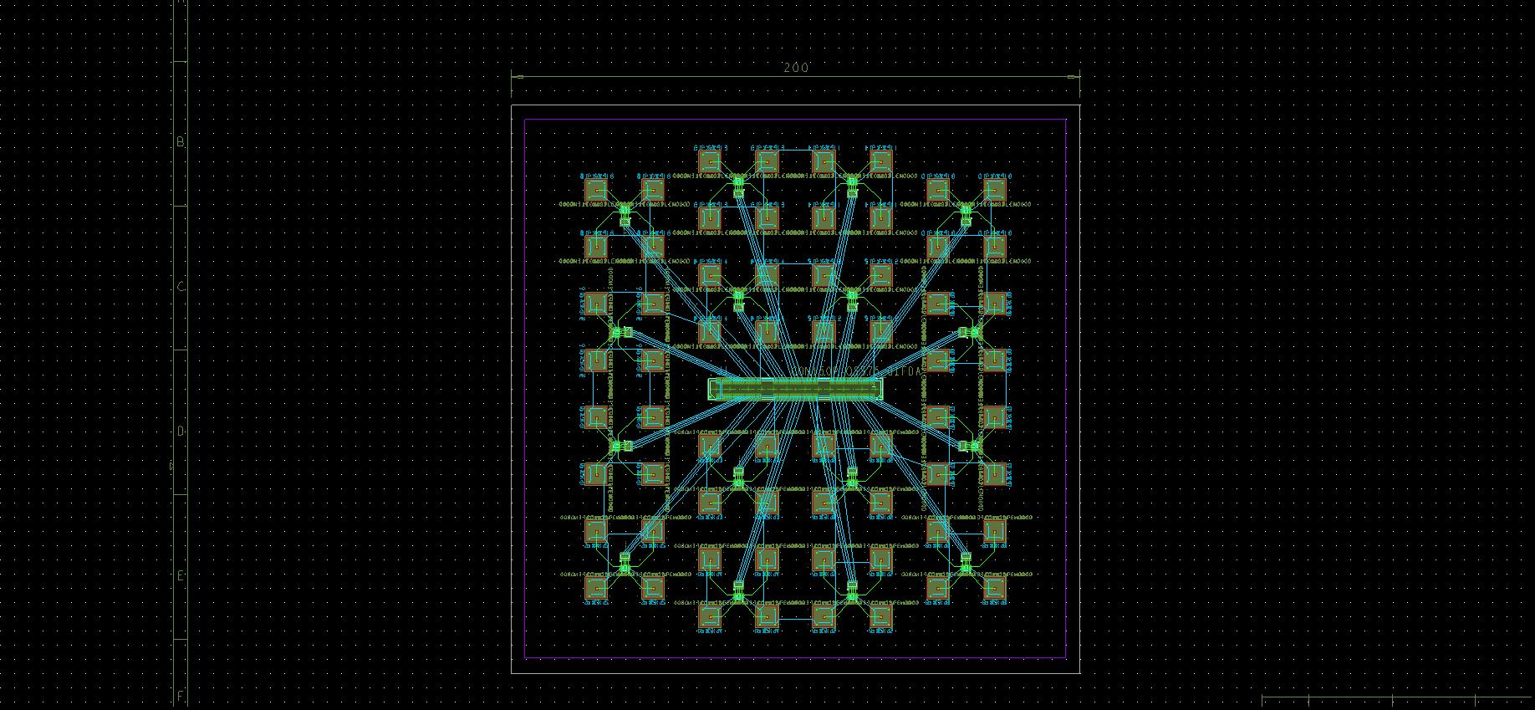
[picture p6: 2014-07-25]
design_files/worklib/pc049a_db/physical/pc049a_lemo_db_placement_04.jpg

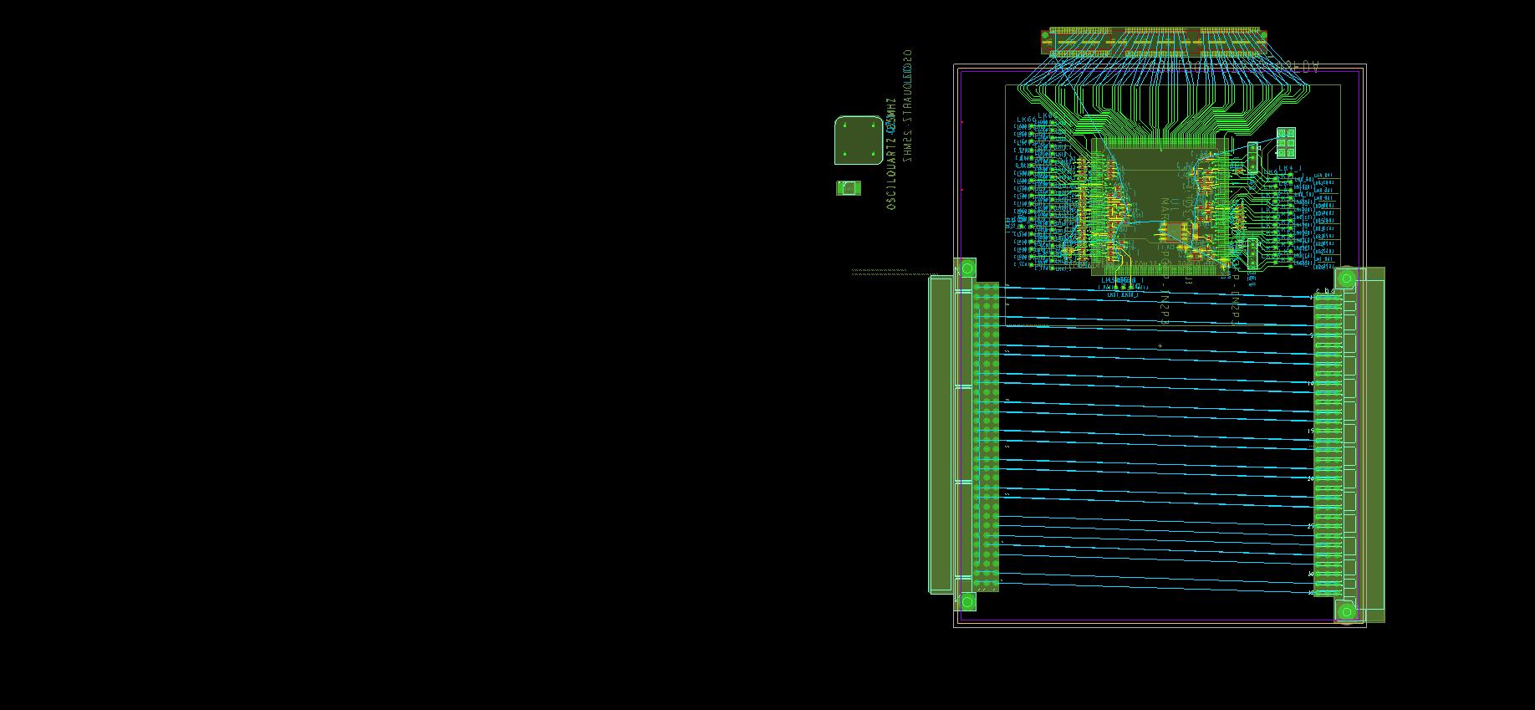
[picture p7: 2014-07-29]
design_files/worklib/pc049a_toplevel/physical/toplevel_single_maroc_01.jpg

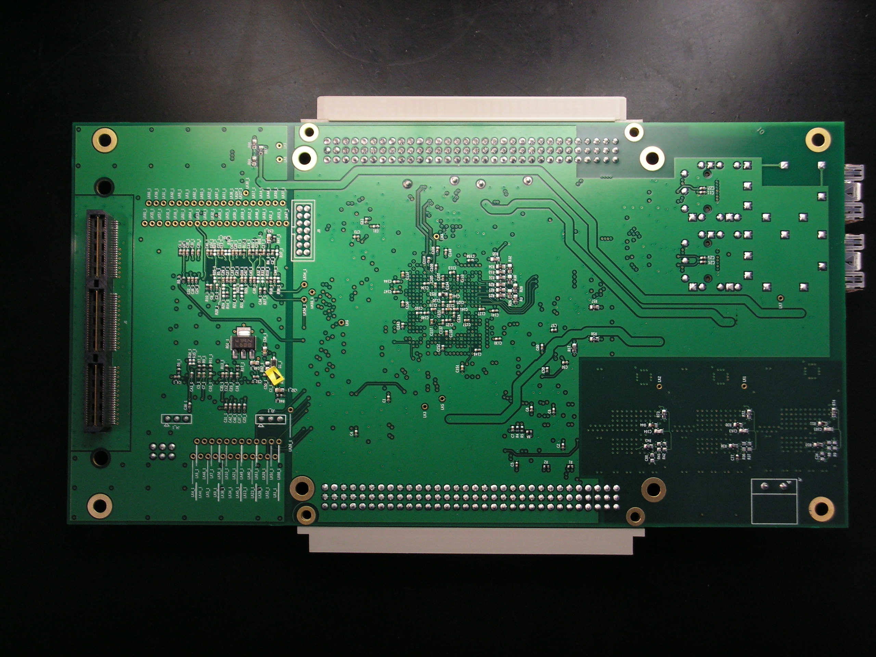
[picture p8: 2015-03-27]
www/Docs/Pictures/pc049a_bottom_PICT1282.JPG

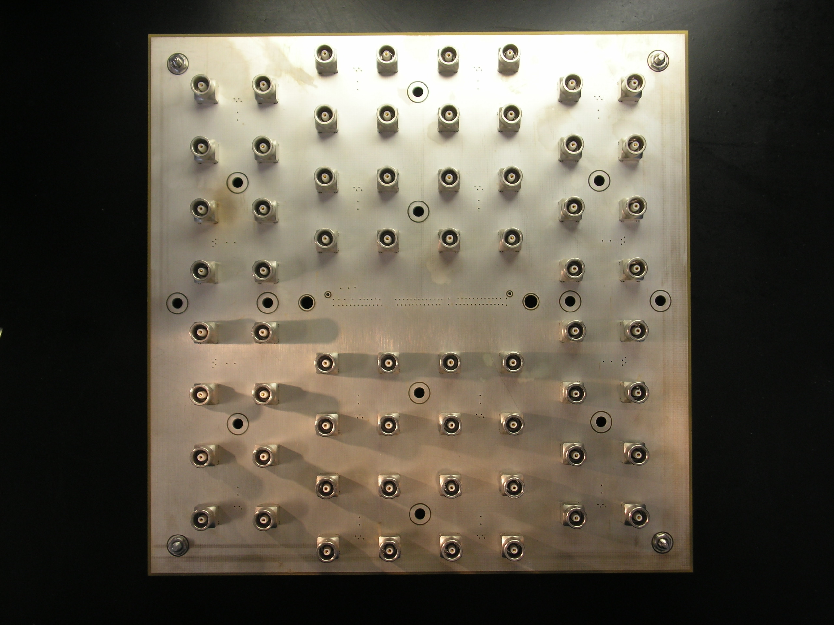
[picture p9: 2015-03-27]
www/Docs/Pictures/pc049a_lemo_adaptor_bottom_PICT1285.JPG

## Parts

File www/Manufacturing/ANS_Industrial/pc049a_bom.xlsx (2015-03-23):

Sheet: Summary
TITLE:" Bill of Materials "DATE:" 07/29/2014 "DESIGN:" pc049a_toplevel "TEMPLATE:" /projects/HEP_Instrumentation/cad/tools/cadence_templates/spreadsheet-format.bom "CALLOUT:
Part Name | Ref Des | Qty | PART_NUMBER | PART_DESCRIPTION | OL_COMMENTS | PL_COMMENTS
24AA64T-I/MC | IC15 | 1 | 24AA64T-I/MC | ? | Farnell: 1331305 | ?
570CAC000121DG | QZ1 | 1 | 570CAC000121DG | ? | Digikey: 336-2519-ND | ?
AD5662BRMZ-1 | IC1,IC9 | 2 | AD5662BRMZ-1 | ? | Farnell: 1117908 | ?
AD8031_SOT23-5-AD | U2 | 1 | AD8031ARTZ-R2 | SIngle Rail-to-rail op-amp, sot23 | Farnell 1319421 | -
BNX022-01 | LC1,LC2,LC3 | 3 | BNX022-01 | ? | Farnell: 1114996 RS: 724-1643 | ?
CAPCERSMDCL1_0603-100PF,50V | C163,C164,C165 | 3 | CC0603_100PF_50V_5%_NP0 | ? | ? | ?
CAPCERSMDCL2_0402-100NF,16V_GEN | C1,C1_1,C2,C2_1,C3_1,C4,C4_1,C5,C5_1,C6,C6_1,C7,C7_1,C8,C8_1,C9_1,C10_1,C11,C11_1,C12_1,C13_1,C14,C14_1,C15,C15_1,C16,C16_1,C17,C17_1,C18,C18_1,C19,C19_1,C20,C20_1,C21,C21_1,C22,C22_1,C23_1,C24_1,C25_1,C26,C26_1,C27_1,C28_1,C29,C29_1,C30_1,C31_1,C32_1,C33_1,C34_1,C35_1,C36_1,C37_1,C38_1,C39_1,C40_1,C41_1,C42_1,C43_1,C44_1,C45,C45_1,C46_1,C47_1,C49,C50,C50_1,C51_1,C56,C57,C58,C60,C61,C62,C63,C64,C66,C68,C69,C70,C72,C73,C77,C105,C106,C108,C109,C111,C112,C113,C114,C120,C121,C122,C123,C124,C125,C128,C130,C131,C132,C134,C137,C140,C141,C143,C144,C146,C147,C149,C150,C152,C154,C156,C158,C159,C160 | 120 | CC0402_100NF_16V_10%_X7R | e.g. GRM155R71C104KA88D | Farnell: 8819742 | ?
CAPCERSMDCL2_0402-1NF_X7R,50V | C44 | 1 | CC0402_1NF_50V_10%_X7R | e.g. GRM155R71H102KA01D | Farnell: 1828882 | ?
CAPCERSMDCL2_0402-1UF,16V | C3,C9,C10,C12,C24,C25,C27,C59,C71,C101,C107,C110 | 12 | CC0402_1UF0_16V_10%_X5R | e.g. GRM155R61C105KA12D | Farnell 2362093 | ?
CAPCERSMDCL2_0402-2.2UF,6.3V | C138 | 1 | CC0402_2UF2_6V3_20%_X5R | ? | ? | ?
CAPCERSMDCL2_0402-4.7UF,4V | C117,C118,C119,C127,C145,C148,C151,C153,C155,C157 | 10 | CC0402_4UF7_4V_10% | e.g. GRM155R60G475ME | Farnell 1735525 | ?
CAPCERSMDCL2_0603-100NF,16V | C31,C100,C103 | 3 | CC0603_100NF_16V_10%_X7R | ? | ? | ?
CAPCERSMDCL2_0603-10UF,6.3V | C48,C48_1,C52_1,C53_1,C54_1 | 5 | CC0603_10UF_6V3_20%_X5R | e.g. GRM188R60J106ME47D | Farnell: 1735528 | ?
CAPCERSMDCL2_0603-2.2UF,10V | C41,C42,C46,C84,C95 | 5 | CC0603_2UF2_10V_10%_Y5V | e.g. GRM188R61C225KE15D | Farnell: 1735526 | ?
CAPCERSMDCL2_0603-22UF,4V | C13,C23,C28,C30 | 4 | CC0603_22UF_4V_20%_X5R | e.g. GRM188R60G226MEA0L | Farnell: 1845732 | ?
CAPCERSMDCL2_0603-4.7UF,6.3V_GEN | C47 | 1 | CC0603_4UF7_6V3_10%_X5R | e.g. GRM188R60J475KE19D | Farnell: 1735527 | ?
CAPCERSMDCL2_0603-XX,50V | C34,C88 | 2 | CC0603_UNSPEC_50V_10%_X7R | ? | ? | Do Not Fit
CAPCERSMDCL2_0805-22UF,6.3V | C43,C51,C52,C53,C54,C55,C65,C67,C74,C98,C99,C104,C129 | 13 | CC0805_22UF_6V3_15%_X7R | e.g GRM21BR60J226ME39L | Farnell: 1735531 | ?
CAPCERSMDCL2_1206-100UF_X5R,6.3V | C96,C97,C115,C116,C126,C133,C136,C139,C142 | 9 | CC1206_100UF_6V3_20%_X5R | e.g. GRM31CR60J107ME39L | Farnell: 1735535 | ?
CAPCERSMDCL2_1210-10UF,50V | C33,C35,C36,C37,C76,C78,C79,C80,C87,C89,C90,C91 | 12 | CC1210_10UF_50V_10%_X7R | e.g. GRM32ER71H106KA12L | Farnell: 2362133 | ?
CAPCERSMDCL2_1210-47UF_X5R | C38,C39,C81,C82,C92,C93 | 6 | CC1210_47UF_20%_X5R | e.g. GRM32ER61C476KE15L | Farnell 1828819 | ?
CDCM61004RHB | IC11 | 1 | CDCM61004RHBT | ? | Farnell: 1710796 | ?
CON12P-TSM-106-01-S-DV | J10 | 1 | TSM-106-01-S-DV | ? | Order from Samtec | ?
CON14P-MOLEX_87831 | J8 | 1 | 87831-1420 | ? | Farnell: 7472285 | ?
CON150P-QTS75_03FDA | J1 | 1 | QTS-075-03-F-D-A | ? | Order from Samtec | Free Issue
CON20P_SFP-1367073-1 | J6,J7 | 2 | 1367073-1 | ? | Farnell: 1629987 | ?
CON2P-MSTBA2,5/2-G-5,08 | J9 | 1 | 1757242 | ? | Farnell: 3705171 RS: 189-6105 | ?
CON3P-SIL254D | J3_1,J4_1 | 2 | MTLW-103-07-L-S-250, alternative: AmpModu 826629-3 | ? | AmpModu 826629-3 : Farnell 3418297 | ?
CON6P-SSW-103-01-G-D | J1_1 | 1 | SSW-103-01-G-D | ? | Farnell: 1668336 | ?
CONABC96-09 03 196 6921 | J2 | 1 | 09 03 196 6921 | ? | Farnell: 1096905 | ?
CONABC96-09 73 296 6801 | J3 | 1 | 09 73 296 6801 | ? | Farnell: 1096942 | ?
DIODE_CA_SCHOTTKY-BAT54HT1G | D1_1 | 1 | BAT54HT1G | ? | Farnell: 1459033 | ? | Original design specified RB751V40T1G
DS18B20U+ | IC13 | 1 | DS18B20U+ | ? | Farnell: 1379725 | ?
DS90LV001TM | IC5,IC6,IC7 | 3 | DS90LV001TM | ? | Farnell 1469017 | ?
DS92001TMA | IC2,IC3 | 2 | DS92001TMA | ? | Farnell 1685783 | ?
ELCAPTAN_SMD-150UF,20V | C32,C75,C86 | 3 | CTE7343-43_150UF_20V_10% | e.g. T491X157K020AT | Farnell 2112979 | ?
ELCAPTAN_SMD-220UF,6.3V | C40,C83,C85,C94 | 4 | 6TPB220ML | e.g. TCJD227M010R0040 | Farnell 2408441 | ?
FERRITE_C0805-LI0805H121R-10,LI0805H121R-10 | L1,L2,L3,L4,L9 | 5 | LI0805H121R-10 | ? | Farnell: 2292438 | ?
FERRITE_SMD-220Z,LI0603G221R | L5,L6,L7,L8 | 4 | LI0603G221R | ? | Farnell 2292434 | ? | Original design specified ILBB-0603-220
LED-HSMG-C150 | LD4,LD6,LD7 | 3 | HSMG-C150 | ? | Farnell: 8554595 | ?
LED-HSMH-C150 | LD1,LD2,LD5 | 3 | HSMH-C150 | ? | Farnell: 8554633 | ?
LED-HSMY-C150 | LD3 | 1 | HSMY-C150 | ? | Farnell: 8554773 | ?
LM2937IMP_SOT223-2.5V,TI | RG1_1 | 1 | TI LM2937IMP-2.5 | 2.5V, 400mA Ultra Low Dropout Regulator | Available from Farnell 9779299 | -
LM4040-CIM3-2.5V,0.5% | Z1 | 1 | LM4040CIM3-2.5 | ? | Farnell 1468840 | ?
LP38692_SOT223-ADJ,TEXAS INSTRUMENTS | IC21 | 1 | LP38692MP-ADJ | Adjustable, 1A Low Dropout Regulator | Available from RS 660-6724, Farnell 1496843 | -
LT1585_TO263-3V3 | REG1 | 1 | LT1585CM-3.3 | ? | DigiKey: LT1585CM-3.3#PBF-ND | ?
LT1585_TO263-ADJ | REG3 | 1 | LT1585CM | ? | Farnell 9560637 | ?
LT3070EUFD#PBF | RG1 | 1 | LT3070EUFD#PBF | ? | RS: 761-8614 , Farnell: 1839227 | ?
LTM4606EV#PBF | IC4,IC10,IC14 | 3 | LTM4606EV#PBF | ? | Farnell: 1647767 DigiKey: LTM4606EV#PBF-ND | ?
MAROC3_PQFP-IN2P3 | U1_1 | 1 | MAROC3 | MAROC3 PMT amplifier | MAROC3 64-input PMT amplifier with built in Wilkinson ADC | Free Issue
MC100EP05_SOIC | U4 | 1 | MC100EP05DG | 3.3v ECL 2-input Differential AND/NAND | Farnell: 1607761 | - | MC100LVEL05DG , RS 787-6775 is an (inferior) alternative
OSC_6P_VCTRL_ENDIS_OUT_124-CFPV-45,20.000MHZ | QZ2 | 1 | 20MHz CFPV-45, LF VCXO026156 | ? | Farnell: 1674677 | ?
OSC_VCXO_4P_OSC_4PIN_53S-25MHZ,MERCURY | U1 | 1 | VM53S3-25.000-2.5/-30+75 | VM53S3-25.000-2.5/-30+75, Voltage Controlled Oscillator, 25MHz 2.75 to 5V, 4-Pin SMD 5x3.2mm surface mount oscillator | RS 672-0797 | -
PC049A_FPGA | U3 | 1 | Xilinx XC6SLX100T-3FGG484C | ? | e.g. Digikey 122-1761-ND
R4ISMD_1206-150 | RN1,RN2,RZ1 | 3 | TC164-JR-07150RL | ? | Farnell 9241205 | Free Issue
R4ISMD_1206-4.7K | RZ2 | 1 | TC164-JR-074K7L | ? | Farnell 9241299 | ?
RSMD0402_-00, | R64,R65 | 2 | R0402_00_JUMPER | ? | ? | ?
RSMD0402_0.0625W-XX,1% | R20_1,R21_1,R22_1,R23_1,R25_1,R26_1,R28_1,R29_1,R30_1,R31_1,R32_1,R33_1,R34_1,R35_1,R36_1,R37_1 | 16 | R0402_XX_1%_0.063W | ? | ? | Do Not Fit
RSMD0402_1/16W-100,1% | R1,R2,R6,R14_1,R17_1,R24_1,R78 | 7 | R0402_100R_1%_0.063W_200PPM | ? | ? | ?
RSMD0402_1/16W-10R,5% | R3_1,R4_1,R5_1,R6_1,R7_1,R8_1,R9_1,R10_1,R11_1,R12_1,R13_1,R15_1,R16_1 | 13 | R0402_10R_5%_0.063W_200PPM | ? | ? | ?
RSMD0402_1/16W-1K,5% | R27_1 | 1 | R0402_1K_5%_0.063W_100PPM | ? | ? | ?
RSMD0402_1/16W-3.3R,5% | R46_1,R47_1 | 2 | R0402_3R3_5%_0.063W_200PPM | ? | ? | ?
RSMD0402_1/16W-33,1% | R77 | 1 | R0402_33R_1%_0.063W_200PPM | ? | ? | ?
RSMD0402_1/16W-47K,1% | R13 | 1 | R0402_47K_1%_0.063W_200PPM | ? | ? | ?
RSMD0402_1/16W-51,1% | R1_1,R2_1,R4,R5,R18_1,R19_1 | 6 | R0402_51R_1%_0.063W_200PPM | ? | ? | ?
RSMD0603_-00, | R20,R21,R54,R55 | 4 | R0603_00_JUMPER | ? | ? | ?
RSMD0603_1/10W-100,1% | R75,R76 | 2 | R0603_100R_1%_0.1W_100PPM | ? | ? | ?
RSMD0603_1/10W-100K,1% | R10,R38,R43,R72,R73,R74 | 6 | R0603_100K_1%_0.1W_100PPM | ? | ? | ?
RSMD0603_1/10W-11K,1% | R44 | 1 | R0603_11K_1%_0.1W_100PPM | ? | ? | ?
RSMD0603_1/10W-120,1% | R46,R47,R51 | 3 | R0603_120R_1%_0.1W_100PPM | ? | ? | ?
RSMD0603_1/10W-150,1% | R52,R70 | 2 | R0603_150R_1%_0.1W_100PPM | ? | ? | ?
RSMD0603_1/10W-180,1% | R50 | 1 | R0603_180R_1%_0.1W_100PPM | ? | ? | ?
RSMD0603_1/10W-2.4K,1% | R63 | 1 | R0603_2K4_1%_0.1W_100PPM | ? | ? | ?
RSMD0603_1/10W-240,1% | R14,R15,R16 | 3 | R0603_240R_1%_0.1W_100PPM | ? | ? | ?
RSMD0603_1/10W-270K,1% | R49 | 1 | R0603_270K_1%_0.1W_100PPM | ? | ? | ?
RSMD0603_1/10W-3.3K,1% | R71 | 1 | R0603_3K3_1%_0.1W_100PPM | ? | ? | ?
RSMD0603_1/10W-300K,1% | R66 | 1 | R0603_300K_1%_0.1W_100PPM | ? | ? | ?
RSMD0603_1/10W-33,1% | R17 | 1 | R0603_33R_1%_0.1W_100PPM | ? | ? | ?
RSMD0603_1/10W-330,1% | R61 | 1 | R0603_330R_1%_0.1W_100PPM | ? | ? | ?
RSMD0603_1/10W-36K,1% | R68 | 1 | R0603_36K_1%_0.1W_100PPM | ? | ? | ?
RSMD0603_1/10W-390K,1% | R12,R40,R45 | 3 | R0603_390K_1%_0.1W_100PPM | ? | ? | ?
RSMD0603_1/10W-4.7K,1% | R7,R48,R56,R57,R58,R59,R60,R62,R67 | 9 | R0603_4K7_1%_0.1W_100PPM | ? | ? | ?
RSMD0603_1/10W-51,1% | R53 | 1 | R0603_51R_1%_0.1W_100PPM | ? | ? | ?
RSMD0603_1/10W-62K,1% | R69 | 1 | R0603_62K_1%_0.1W_100PPM | ? | ? | ?
RSMD0603_1/10W-82,1% | R42_1 | 1 | R0603_82R_1%_0.1W_100PPM | ? | ? | ?
RSMD0603_1/10W-XX,1% | R8,R9,R18,R19,R22,R23,R24,R36,R37,R41,R42 | 11 | R0603_XX_1%_0.1W_100PPM | ? | ? | Do Not Fit
RSMD0603_1/16W-1.2K,1% | R26,R28,R30,R32,R34 | 5 | R0603_1K2_1%_0.063W_100PPM | ? | ? | ?
RSMD0603_1/16W-2.4K,1% | R3,R25,R27,R29,R31,R33,R35 | 7 | R0603_2K4_1%_0.063W_100PPM | ? | ? | ?
RSMD0603_1/16W-40.2K,1% | R39 | 1 | R0603_40K2_1%_0.063W_100PPM | ? | ? | ?
RSMD0603_1/16W-9K,1% | R11 | 1 | R0603_9K_1%_0.063W_100PPM | ? | ? | ?
RSMD0805_-00, | R79,R80 | 2 | R0805_00_JUMPER | ? | ? | ?
S25FL128SAGMFIR01 | IC22 | 1 | S25FL128SAGMFIR01 | ? | Farnell: 2400295 (extended range) Mouser: 797-25FL128SAGMFIR00 or 797-25FL128SAGMFIR01 DigiKey: 1274-1047-ND | ?
SFP_CAGE-6367034-1 | SFP1,SFP3 | 2 | 6367034-1 | ? | Farnell: 2399755 | ?
SFP_CAGE-6367035-1 | SFP2,SFP4 | 2 | 6367035-1 | ? | Farnell 1629986 | ?
SK_SATA_SMD_STR-MOLEX | J4,J5 | 2 | Molex 67800-5025 | MOLEX - 67800-5025 - HEADER, SATA, SMT vertical, 1.27MM, 7WAY | Farnell: 1629985 | -
SN65LVDS1_SOT23-5-TEXAS INSTRUMENTS | U5 | 1 | snlvds1dbv | single high speed differential line driver | RS 462-0210, Farnell 8452482 | -
SN74LVC1G06DBVT | IC16 | 1 | SN74LVC1G06DBVT or SN74LVC1G06DBVR | ? | SN74LVC1G06DBVR: Farnell 1105928 | ?
SW4INT-1571983-4 | SW3 | 1 | 1571983-4 / GDH04S04 | ? | GDH04S04: Farnell 1123953 | ?
SW_PUSHBUTTON_1SPSTA_4P_1-OMRON_B3SN-3012 | SW1,SW2,SW4 | 3 | b3sn-3012 | ? | Farnell: 1181018 | ?
TPS71701DCKRG4_SC70-TEXAS INSTRUMENTS | IC20 | 1 | TI tps71701dckrg4 | 0.9V - 6.2V adjustable LDO 150mA linear regulator | RS 661-3801 , Farnell 1703393 | -
TOTAL |  | 409

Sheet: One Per Line
 | position of pin 1 |  | rotation | Top (blank) or bottom (m) | Package
Ref Des | x | y
C1 | 64.165 | 117.541 | 0 | m | C0402
C1_1 | 58.7507 | 149.2061 | 0 | m | C0402
C10 | 4.829 | 46.017 | 0 |  | C0402
C10_1 | 57.0968 | 166.0878 | 180 | m | C0402
C100 | 36.432 | 70.785 | 270 |  | C0603
C101 | 67.575 | 111.751 | 0 |  | C0402
C103 | 73.939 | 122.956 | 180 |  | C0603
C104 | 21.278 | 108.195 | 0 |  | C0805
C105 | 33.392 | 104.853 | 0 | m | C0402
C106 | 22.744 | 104.385 | 180 | m | C0402
C107 | 30.491 | 102.861 | 180 | m | C0402
C108 | 22.492 | 106.353 | 0 |  | C0402
C109 | 27.57 | 104.766 | 180 | m | C0402
C11 | 10.809 | 40.81 | 180 |  | C0402
C11_1 | 23.545 | 158.1995 | 180 | m | C0402
C110 | 30.491 | 98.797 | 180 | m | C0402
C111 | 22.992 | 96.853 | 0 |  | C0402
C112 | 22.998 | 98.67 | 0 |  | C0402
C113 | 29.442 | 99.903 | 270 | m | C0402
C114 | 25.538 | 106.798 | 180 | m | C0402
C115 | 16.844 | 107.409 | 270 |  | C1206
C116 | 23.932 | 102.099 | 180 |  | C1206
C117 | 42.429 | 105.909 | 180 | m | C0402
C118 | 39.442 | 100.903 | 270 | m | C0402
C119 | 39.45 | 105.851 | 90 | m | C0402
C12 | 10.809 | 39.794 | 180 |  | C0402
C12_1 | 57.045 | 161.6995 | 180 | m | C0402
C120 | 38.392 | 102.853 | 0 | m | C0402
C121 | 42.442 | 101.803 | 90 | m | C0402
C122 | 40.392 | 102.853 | 0 | m | C0402
C123 | 22.998 | 94.352 | 0 |  | C0402
C124 | 40.524 | 99.813 | 180 | m | C0402
C125 | 37.418 | 99.871 | 270 | m | C0402
C126 | 41.942 | 85.853 | 90 |  | C1206
C127 | 39.442 | 91.903 | 270 | m | C0402
C128 | 17.442 | 65.903 | 90 |  | C0402
C129 | 31.442 | 129.953 | 90 |  | C0805
C13 | 11.109 | 42.08 | 180 |  | C0603
C13_1 | 23.545 | 163.1995 | 180 | m | C0402
C130 | 47.451 | 87.425 | 270 | m | C0402
C131 | 11.576 | 45.173 | 90 |  | C0402
C132 | 28.942 | 45.3 | 90 |  | C0402
C133 | 20.043 | 110.608 | 0 |  | C1206
C134 | 32.442 | 106.903 | 270 | m | C0402
C136 | 33.354 | 120.998 | 270 |  | C1206
C137 | 42.492 | 102.853 | 180 | m | C0402
C138 | 42.879 | 117.535 | 270 |  | C0402
C139 | 58.095 | 88.891 | 180 |  | C1206
C14 | 34.942 | 77.903 | 90 |  | C0402
C14_1 | 23.545 | 155.6995 | 180 | m | C0402
C140 | 40.45 | 107.756 | 90 | m | C0402
C141 | 39.831 | 88.314 | 270 | m | C0402
C142 | 19.942 | 91.853 | 0 |  | C1206
C143 | 44.345 | 113.783 | 0 | m | C0402
C144 | 31.957 | 116.011 | 90 | m | C0402
C145 | 39.45 | 99.755 | 90 | m | C0402
C146 | 50.461 | 92.988 | 270 | m | C0402
C147 | 34.751 | 116.011 | 90 | m | C0402
C148 | 36.471 | 100.829 | 0 | m | C0402
C149 | 23.379 | 102.099 | 180 | m | C0402
C15 | 12.315 | 124.857 | 180 |  | C0402
C15_1 | 23.545 | 153.6995 | 180 | m | C0402
C150 | 22.363 | 89.653 | 0 |  | C0402
C151 | 55.912 | 97.574 | 0 | m | C0402
C152 | 50.363 | 102.869 | 0 | m | C0402
C153 | 29.602 | 113.783 | 180 | m | C0402
C154 | 32.492 | 102.853 | 180 | m | C0402
C155 | 46.392 | 101.853 | 0 | m | C0402
C156 | 37.603 | 113.783 | 180 | m | C0402
C157 | 42.442 | 95.903 | 270 | m | C0402
C158 | 26.115 | 95.818 | 90 | m | C0402
C159 | 55.02 | 109.368 | 180 |  | C0402
C16 | 8.266 | 88.891 | 0 |  | C0402
C16_1 | 57.0891 | 158.7029 | 180 | m | C0402
C160 | 40.466 | 108.888 | 270 | m | C0402
C163 | 72.208 | 22.3576 | 90 | m | C0603
C164 | 72.3604 | 45.2938 | 90 | m | C0603
C165 | 71.708 | -0.402 | 90 | m | C0603
C17 | 8.393 | 104.131 | 0 |  | C0402
C17_1 | 23.545 | 151.6995 | 180 | m | C0402
C18 | 8.266 | 87.875 | 0 |  | C0402
C18_1 | 23.545 | 172.6995 | 180 | m | C0402
C19 | 12.333 | 127.805 | 180 |  | C0402
C19_1 | 31.945 | 157.6995 | 0 | m | C0402
C2 | 76.892 | 70.353 | 0 | m | C0402
C2_1 | 23.5339 | 149.3548 | 180 | m | C0402
C20 | 8.301 | 105.162 | 0 |  | C0402
C20_1 | 23.545 | 169.6995 | 180 | m | C0402
C21 | 12.333 | 125.773 | 180 |  | C0402
C21_1 | 31.945 | 159.6995 | 0 | m | C0402
C22 | 6.353 | 39.794 | 0 |  | C0402
C22_1 | 23.545 | 164.1995 | 180 | m | C0402
C23 | 6.053 | 42.08 | 0 |  | C0603
C23_1 | 57.0664 | 160.3784 | 180 | m | C0402
C24 | 22.413 | 46.106 | 0 |  | C0402
C24_1 | 23.545 | 166.1995 | 180 | m | C0402
C25 | 22.413 | 45.106 | 0 |  | C0402
C25_1 | 66.445 | 156.6995 | 0 | m | C0402
C26 | 28.335 | 39.921 | 180 |  | C0402
C26_1 | 23.545 | 159.1995 | 180 | m | C0402
C27 | 28.335 | 40.937 | 180 |  | C0402
C27_1 | 31.945 | 161.6995 | 0 | m | C0402
C28 | 28.635 | 42.207 | 180 |  | C0603
C28_1 | 31.945 | 170.1995 | 0 | m | C0402
C29 | 24.006 | 39.921 | 0 |  | C0402
C29_1 | 31.045 | 162.6995 | 180 | m | C0402
C3 | 16.555 | 83.932 | 0 |  | C0402
C3_1 | 33.8688 | 164.4966 | 0 | m | C0402
C30 | 23.579 | 42.207 | 0 |  | C0603
C30_1 | 31.9476 | 154.2606 | 0 | m | C0402
C31 | 35.64 | 87.99 | 270 |  | C0603
C31_1 | 66.4453 | 161.7978 | 0 | m | C0402
C32 | 75.3576 | 14.9528 | 0 |  | C7343POL
C32_1 | 31.9425 | 172.2447 | 0 | m | C0402
C33 | 81.8518 | 6.966 | 180 |  | CAPC3225X279N
C33_1 | 31.945 | 160.6995 | 0 | m | C0402
C34 | 79.7398 | 0.5764 | 0 | m | C0603
C34_1 | 34.925 | 152.6395 | 0 | m | C0402
C35 | 81.836 | 10.4316 | 180 |  | CAPC3225X279N
C35_1 | 57.045 | 162.6995 | 180 | m | C0402
C36 | 81.8574 | 3.4302 | 180 |  | CAPC3225X279N
C36_1 | 31.9501 | 171.2202 | 0 | m | C0402
C37 | 81.8614 | -0.0586 | 180 |  | CAPC3225X279N
C37_1 | 66.445 | 158.1995 | 0 | m | C0402
C38 | 70.7348 | 16.4274 | 270 |  | C1210
C38_1 | 66.2134 | 171.7246 | 0 | m | C0402
C39 | 66.747 | 16.4274 | 270 |  | C1210
C39_1 | 23.5556 | 171.3302 | 180 | m | C0402
C4 | 73.547 | 126.281 | 0 | m | C0402
C4_1 | 57.995 | 175.6495 | 90 | m | C0402
C40 | 63.1816 | 14.7726 | 180 |  | POSCAP_D3
C40_1 | 23.545 | 167.1995 | 180 | m | C0402
C41 | 41.347 | 1.555 | 270 |  | C0603
C41_1 | 31.945 | 156.6995 | 0 | m | C0402
C42 | 14.157 | 104.437 | 180 |  | C0603
C42_1 | 66.4341 | 160.5909 | 0 | m | C0402
C43 | 4.398 | 156.847 | 270 |  | C0805
C43_1 | 57.045 | 171.1995 | 180 | m | C0402
C44 | 9.282 | 102.607 | 0 |  | C0402
C44_1 | 31.9361 | 148.7228 | 0 | m | C0402
C45 | 9.282 | 100.575 | 0 |  | C0402
C45_1 | 31.9361 | 155.2759 | 0 | m | C0402
C46 | 17.987 | 97.793 | 90 |  | C0603
C46_1 | 66.4341 | 159.4063 | 0 | m | C0402
C47 | 19.257 | 97.793 | 90 |  | C0603
C47_1 | 23.545 | 160.1995 | 180 | m | C0402
C48 | 20.527 | 97.793 | 90 |  | C0603
C48_1 | 54.155 | 153.2895 | 270 | m | C0603
C49 | 12.333 | 128.821 | 180 |  | C0402
C5 | 80.992 | 82.853 | 180 | m | C0402
C5_1 | 57.045 | 169.1995 | 180 | m | C0402
C50 | 53.833 | 69.316 | 270 | m | C0402
C50_1 | 57.3555 | 151.2793 | 90 | m | C0402
C51 | 53.835 | 70.663 | 270 |  | C0805
C51_1 | 57.9132 | 154.0932 | 90 | m | C0402
C52 | 52.942 | 81.253 | 270 |  | C0805
C52_1 | 61.5256 | 146.4027 | 270 | m | C0603
C53 | 54.942 | 81.253 | 270 |  | C0805
C53_1 | 19.483 | 150.3896 | 180 | m | C0603
C54 | 59.942 | 81.253 | 270 |  | C0805
C54_1 | 50.1699 | 151.2392 | 180 | m | C0603
C55 | 61.942 | 81.253 | 270 |  | C0805
C56 | 45.546 | 82.102 | 270 |  | C0402
C57 | 45.038 | 73.212 | 90 | m | C0402
C58 | 56.315 | 74.592 | 0 | m | C0402
C59 | 49.942 | 82.803 | 270 |  | C0402
C6 | 67.392 | 72.853 | 0 | m | C0402
C6_1 | 23.545 | 174.6995 | 180 | m | C0402
C60 | 49.2 | 75.989 | 180 | m | C0402
C61 | 16.836 | 120.751 | 270 | m | C0402
C62 | 25.484 | 126.323 | 270 |  | C0402
C63 | 15.718 | 123.808 | 0 | m | C0402
C64 | 11.366 | 123.681 | 0 |  | C0402
C65 | 23.884 | 126.381 | 180 |  | C0805
C66 | 11.433 | 126.789 | 0 |  | C0402
C67 | 23.884 | 121.873 | 180 |  | C0805
C68 | 11.389 | 129.904 | 0 |  | C0402
C69 | 22.934 | 123.881 | 180 |  | C0402
C7 | 71.385 | 83.938 | 180 | m | C0402
C7_1 | 57.0457 | 167.8937 | 180 | m | C0402
C70 | 16.074 | 131.684 | 270 |  | C0402
C71 | 22.934 | 124.881 | 180 |  | C0402
C72 | 17.852 | 131.684 | 270 |  | C0402
C73 | 19.69 | 126.925 | 90 | m | C0402
C74 | 38.55 | 8.754 | 0 |  | C0805
C75 | 75.7386 | 37.6858 | 0 |  | C7343POL
C76 | 82.2424 | 33.19 | 180 |  | CAPC3225X279N
C77 | 79.8462 | 23.3094 | 0 | m | C0402
C78 | 82.2678 | 29.6848 | 180 |  | CAPC3225X279N
C79 | 82.2678 | 26.1796 | 180 |  | CAPC3225X279N
C8 | 66.892 | 78.853 | 0 | m | C0402
C8_1 | 23.545 | 173.6995 | 180 | m | C0402
C80 | 82.2678 | 22.6744 | 180 |  | CAPC3225X279N
C81 | 71.1412 | 39.1858 | 270 |  | C1210
C82 | 67.128 | 39.1604 | 270 |  | C1210
C83 | 63.4102 | 37.5056 | 180 |  | POSCAP_D3
C84 | 41.2896 | 23.351 | 0 |  | C0603
C85 | 10.621 | 94.098 | 0 |  | POSCAP_D3
C86 | 75.9056 | 60.6154 | 0 |  | C7343POL
C87 | 82.4056 | 52.6154 | 180 |  | CAPC3225X279N
C88 | 80.2906 | 46.2504 | 0 | m | C0603
C89 | 82.4056 | 56.1154 | 180 |  | CAPC3225X279N
C9 | 4.829 | 45.001 | 0 |  | C0402
C9_1 | 33.8763 | 166.1191 | 0 | m | C0402
C90 | 82.4056 | 45.6154 | 180 |  | CAPC3225X279N
C91 | 82.4056 | 49.1154 | 180 |  | CAPC3225X279N
C92 | 67.263 | 62.07 | 270 |  | C1210
C93 | 71.327 | 62.07 | 270 |  | C1210
C94 | 63.453 | 60.443 | 180 |  | POSCAP_D3
C95 | 43.0488 | 46.9448 | 270 |  | C0603
C96 | 66.271 | 103.115 | 0 |  | C1206
C97 | 63.707 | 104.663 | 90 |  | C1206
C98 | 2.239 | 156.847 | 270 |  | C0805
C99 | 36.275 | 15.369 | 270 |  | C0805
D1_1 | 52.855 | 148.7395 | 0 | m | SOD323_INV
IC1 | 58.833 | 71.619 | 0 |  | SOP65P490X95-8N
IC10 | 68.9314 | 3.6244 | 270 |  | LGA133S127P12X12_05-08-1766
IC11 | 14.611 | 127.98 | 0 |  | QFN50P500X500X100-33N-S355
IC13 | 68.058 | 117.559 | 180 |  | SOP65P490X110-8N
IC14 | 69.4902 | 49.2936 | 270 |  | LGA133S127P12X12_05-08-1766
IC15 | 38.317 | 68.035 | 90 |  | SON50P300X200X100-9N-R175X155
IC16 | 53.525 | 119.441 | 270 |  | SOT23_5
IC2 | 81.592 | 66.448 | 180 |  | SOIC127P600X175-8N
IC20 | 35.125 | 131.4 | 270 |  | SC70
IC21 | -4.875 | 152.9 | 0 |  | SOT223_5
IC22 | 73.339 | 125.011 | 180 |  | SOIC127P1030X265-16N
IC3 | 81.592 | 72.948 | 180 |  | SOIC127P600X175-8N
IC4 | 69.3378 | 26.3574 | 270 |  | LGA133S127P12X12_05-08-1766
IC5 | 72.092 | 66.448 | 180 |  | SOIC127P600X175-8N
IC6 | 72.092 | 72.948 | 180 |  | SOIC127P600X175-8N
IC7 | 76.292 | 82.758 | 0 |  | SOIC127P600X175-8N
IC9 | 58.833 | 76.619 | 0 |  | SOP65P490X95-8N
J1 | 70.745 | 198.986 | 270 | m | CON150_QTSDA
J1_1 | 76.985 | 176.4995 | 270 |  | SAMTEC_SSW-103-01-G-D
J10 | 14.239 | 54.755 | 90 |  | SAMTEC_TSM-106-01-X-DV
J2 | 95.365 | 139.72 | 0 |  | HARTING_0903196X921
J3 | -9.115 | 50.82 | 180 |  | HARTING_09732966801
J3_1 | 69.387 | 152.0555 | 270 |  | CONHE13D3X1M
J4 | 4.251 | 90.162 | 0 |  | SK_SATA_SMD_STR
J4_1 | 69.387 | 177.7095 | 270 |  | CONHE13D3X1M
J5 | 4.251 | 110.162 | 0 |  | SK_SATA_SMD_STR
J6 | 3.73 | 26.8 | 90 |  | TYCO_1367073
J7 | 22.73 | 26.8 | 90 |  | TYCO_1367073
J8 | 23.948 | 142.029 | 270 |  | CON14MD_2MM
J9 | 87.125 | 10.9 | 180 |  | CON2MC_508
L1 | 9.724 | 45.774 | 270 |  | INDC2012X90N
L2 | 7.438 | 43.974 | 90 |  | INDC2012X90N
L3 | 27.25 | 45.901 | 270 |  | INDC2012X90N
L4 | 24.964 | 44.101 | 90 |  | INDC2012X90N
L5 | 56.692 | 81.353 | 0 |  | C0603
L6 | 61.942 | 83.103 | 90 |  | C0603
L7 | 48.442 | 81.603 | 90 |  | C0603
L8 | 25.496 | 123.238 | 0 |  | C0603
L9 | 23.342 | 104.353 | 180 |  | INDC2012X90N
LC1 | 56.0306 | -1.295 | 180 |  | MURATA_BNX02
LC2 | 57.58 | 23.343 | 180 |  | MURATA_BNX02
LC3 | 57.7324 | 44.1202 | 180 |  | MURATA_BNX02
LD1 | 58.402 | 120.837 | 270 |  | D1206
LD2 | 22.432 | 79.448 | 270 |  | D1206
LD3 | 19.432 | 79.448 | 270 |  | D1206
LD4 | 16.432 | 79.448 | 270 |  | D1206
LD5 | 13.432 | 79.448 | 270 |  | D1206
LD6 | 25.432 | 79.448 | 270 |  | D1206
LD7 | 94.7886 | 24.8588 | 90 |  | D1206
QZ1 | 36.876 | 74.348 | 0 |  | OSC_SILABS_SI570
QZ2 | 45.872 | 72.327 | 0 |  | OSCSC254P490X696X180-6N
R1 | 81.942 | 68.803 | 90 | m | C0402
R1_1 | 65.635 | 151.5475 | 0 |  | C0402
R10 | 75.891 | 2.3932 | 90 | m | C0603
R10_1 | 32.9763 | 167.1576 | 180 | m | C0402
R11 | 70.2014 | 1.1232 | 90 | m | C0603
R11_1 | 55.9864 | 166.0878 | 0 | m | C0402
R12 | 80.5526 | -2.8272 | 180 |  | C0603
R12_1 | 24.445 | 157.1995 | 0 | m | C0402
R13 | 10.182 | 101.591 | 180 |  | C0402
R13_1 | 55.945 | 161.6995 | 0 | m | C0402
R14 | 55.345 | 72.306 | 180 |  | C0603
R14_1 | 35.0625 | 161.6673 | 180 | m | C0402
R15 | 51.4 | 74.286 | 0 |  | C0603
R15_1 | 24.445 | 154.6995 | 0 | m | C0402
R16 | 55.115 | 74.592 | 0 |  | C0603
R16_1 | 24.445 | 152.6995 | 0 | m | C0402
R17 | 50.654 | 67.226 | 0 | m | C0603
R17_1 | 55.945 | 158.6995 | 0 | m | C0402
R18 | 20.519 | 132.111 | 270 |  | C0603
R18_1 | 31.945 | 149.7495 | 0 | m | C0402
R19 | 17.471 | 120.07 | 90 |  | C0603
R19_1 | 31.945 | 150.7595 | 0 | m | C0402
R2 | 81.942 | 75.303 | 90 | m | C0402
R2_1 | 65.635 | 152.8175 | 0 |  | C0402
R20 | 20.265 | 120.07 | 90 |  | C0603
R20_1 | 33.045 | 157.6995 | 180 | m | C0402
R21 | 14.423 | 120.07 | 90 |  | C0603
R21_1 | 35.945 | 157.6995 | 0 | m | C0402
R22 | 19.122 | 132.111 | 270 |  | C0603
R22_1 | 33.045 | 159.6995 | 180 | m | C0402
R23 | 18.868 | 120.07 | 90 |  | C0603
R23_1 | 35.945 | 159.6995 | 0 | m | C0402
R24 | 15.82 | 120.07 | 90 |  | C0603
R24_1 | 63.799 | 150.7275 | 270 |  | C0402
R25 | 35.688 | 86.46 | 270 | m | C0603
R25_1 | 31.0324 | 165.1165 | 180 | m | C0402
R26 | 35.938 | 84.71 | 0 | m | C0603
R26_1 | 23.545 | 165.1995 | 180 | m | C0402
R27 | 34.188 | 86.46 | 270 | m | C0603
R27_1 | 34.005 | 151.3895 | 180 | m | C0402
R28 | 34.438 | 83.21 | 0 | m | C0603
R28_1 | 33.945 | 162.6995 | 0 | m | C0402
R29 | 32.688 | 86.46 | 270 | m | C0603
R29_1 | 35.945 | 162.6995 | 0 | m | C0402
R3 | 37.406 | 83.176 | 0 | m | C0603
R3_1 | 58.7835 | 147.9388 | 0 | m | C0402
R30 | 32.057 | 84.71 | 0 | m | C0603
R30_1 | 24.445 | 161.1995 | 0 | m | C0402
R31 | 30.807 | 86.46 | 270 | m | C0603
R31_1 | 23.545 | 162.1995 | 180 | m | C0402
R32 | 29.057 | 84.71 | 0 | m | C0603
R32_1 | 31.0476 | 153.2569 | 180 | m | C0402
R33 | 29.307 | 86.46 | 270 | m | C0603
R33_1 | 31.9476 | 152.0109 | 0 | m | C0402
R34 | 27.807 | 86.46 | 270 | m | C0603
R34_1 | 54.445 | 171.6995 | 0 | m | C0402
R35 | 25.807 | 87.96 | 270 | m | C0603
R35_1 | 53.545 | 170.6995 | 180 | m | C0402
R36 | 77.1744 | 21.506 | 0 | m | C0603
R36_1 | 31.0246 | 147.7191 | 180 | m | C0402
R37 | 75.6744 | 20.0328 | 180 | m | C0603
R37_1 | 23.5443 | 148.1433 | 180 | m | C0402
R38 | 76.2974 | 25.1262 | 90 | m | C0603
R39 | 70.6078 | 23.8562 | 90 | m | C0603
R4 | 72.285 | 82.668 | 0 | m | C0402
R4_1 | 23.5443 | 150.5662 | 180 | m | C0402
R40 | 80.959 | 19.9058 | 180 |  | C0603
R41 | 77.284 | 44.441 | 0 | m | C0603
R42 | 75.784 | 42.917 | 180 | m | C0603
R42_1 | 55.7021 | 150.5105 | 0 | m | C0603
R43 | 76.4498 | 48.0624 | 90 | m | C0603
R44 | 70.7602 | 46.7924 | 90 | m | C0603
R45 | 81.1114 | 42.842 | 180 |  | C0603
R46 | 66.12 | 111.739 | 270 |  | C0603
R46_1 | 62.9743 | 146.7405 | 270 | m | C0402
R47 | 64.711 | 110.227 | 180 |  | C0603
R47_1 | 19.7509 | 149.0089 | 180 | m | C0402
R48 | 33.341 | 131.597 | 270 |  | C0603
R49 | 38.929 | 130.097 | 90 |  | C0603
R5 | 72.285 | 81.398 | 0 | m | C0402
R5_1 | 31.0476 | 163.9055 | 180 | m | C0402
R50 | 17.005 | 87.682 | 270 |  | C0603
R51 | 20.255 | 87.932 | 180 |  | C0603
R52 | 60.913 | 121.01 | 270 |  | C0603
R53 | 23.817 | 100.194 | 180 |  | C0603
R54 | 55.311 | 110.853 | 180 |  | C0603
R55 | 51.769 | 118.343 | 270 |  | C0603
R56 | 45.942 | 88.603 | 270 |  | C0603
R57 | 38.815 | 62.59 | 90 | m | C0603
R58 | 47.451 | 62.59 | 90 | m | C0603
R59 | 44.442 | 88.603 | 270 |  | C0603
R6 | 72.597 | 79.943 | 90 | m | C0402
R6_1 | 56.8478 | 174.7564 | 0 | m | C0402
R60 | 55.192 | 93.353 | 0 |  | C0603
R61 | 54.956 | 115.307 | 0 |  | C0603
R62 | 55.186 | 96.309 | 0 |  | C0603
R63 | 55.192 | 94.853 | 0 |  | C0603
R64 | 45.442 | 117.565 | 270 |  | C0402
R65 | 44.442 | 117.565 | 270 |  | C0402
R66 | 38.929 | 127.303 | 90 |  | C0603
R67 | -3.361 | 152.899 | 0 | m | C0603
R68 | -6.512 | 154.677 | 180 | m | C0603
R69 | -1.813 | 154.677 | 180 | m | C0603
R7 | 66.624 | 115.763 | 180 |  | C0603
R7_1 | 55.945 | 169.1995 | 0 | m | C0402
R70 | 25.432 | 72.698 | 90 |  | C0603
R71 | 94.7124 | 31.8064 | 270 |  | C0603
R72 | 66.894 | 20.057 | 180 | m | C0603
R73 | 67.021 | 43.044 | 180 | m | C0603
R74 | 66.386 | -2.676 | 180 | m | C0603
R75 | 49.942 | 116.833 | 90 |  | C0603
R76 | 48.442 | 118.333 | 270 |  | C0603
R77 | 72.504 | 135.583 | 180 |  | C0402
R78 | 14.31 | 130.793 | 0 |  | C0402
R79 | 84.662 | 66.528 | 90 |  | C0805
R8 | 76.776 | -1.406 | 0 | m | C0603
R8_1 | 31.045 | 173.6995 | 180 | m | C0402
R80 | 1.225 | 64.9 | 0 |  | C0805
R9 | 75.276 | -2.803 | 180 | m | C0603
R9_1 | 55.9353 | 167.8937 | 0 | m | C0402
REG1 | 39.592 | 16.045 | 0 |  | TO254P1435X460-4N
REG3 | 68.514 | 110.261 | 0 |  | TO254P1435X460-4N
RG1 | 11.9912 | 101.7674 | 0 |  | QFN50P400X500X80-29N-R375X275
RG1_1 | 51.79 | 159.376 | 90 | m | SOT223_4
RN1 | 17.615 | 59.645 | 270 |  | ARC241_SO8
RN2 | 4.115 | 59.645 | 270 |  | ARC241_SO8
RZ1 | 17.94 | 71.194 | 0 |  | ARC241_SO8
RZ2 | 29.702 | 79.218 | 0 |  | ARC241_SO8
SFP1 | 19 | 0 | 90 |  | TYCO_6367034-1
SFP2 | 21.33 | 37.1 | 90 |  | TYCO_6367035-1
SFP3 | 0 | 0 | 90 |  | TYCO_6367034-1
SFP4 | 2.33 | 37.1 | 90 |  | TYCO_6367035-1
SW1 | 42.847 | 61.811 | 90 |  | OMRON_B3SN-3012
SW2 | 51.483 | 61.811 | 90 |  | OMRON_B3SN-3012
SW3 | 29.297 | 68.402 | 90 |  | SW_TYCO_1571983-4
SW4 | 64.567 | 98.918 | 90 |  | OMRON_B3SN-3012
U1 | 46.148 | 75.994 | 90 |  | OSC_4PIN_53S
U1_1 | 59.495 | 178.9795 | 270 |  | PQFP240_050
U2 | 20.7496 | 83.9922 | 180 |  | SOT23-5
U3 | 39.442 | 102.853 | 90 |  | BGA484C100P22X22_2300X2300X260
U4 | 71.942 | 78.853 | 90 |  | SOIC8
U5 | 44.5046 | 81.2202 | 180 |  | SOT23-5
Z1 | 55.446 | 70.7028 | 0 |  | SOT23

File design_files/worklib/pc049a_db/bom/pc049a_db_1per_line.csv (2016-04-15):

TITLE: Bill of Materials
DATE: 04/14/2016
DESIGN: pc049a_db
TEMPLATE: /projects/HEP_Instrumentation/cad/tools/cadence_templates/spreadsheet-format_1per_line.bom
CALLOUT:
Part Name | Ref Des | Qty | PART_NUMBER | PART_DESCRIPTION | OL_COMMENTS | KL_COMMENTS | PL_COMMENTS
CAPN4I-100NF,16V,X7R,CKCA43 | CN16 | 1 | CKCA43X7R1C104M | ? | ? | ? | ?
CAPN4I-100NF,16V,X7R,CKCA43 | CN15 | 1 | CKCA43X7R1C104M | ? | ? | ? | ?
CAPN4I-100NF,16V,X7R,CKCA43 | CN14 | 1 | CKCA43X7R1C104M | ? | ? | ? | ?
CAPN4I-100NF,16V,X7R,CKCA43 | CN13 | 1 | CKCA43X7R1C104M | ? | ? | ? | ?
CAPN4I-100NF,16V,X7R,CKCA43 | CN12 | 1 | CKCA43X7R1C104M | ? | ? | ? | ?
CAPN4I-100NF,16V,X7R,CKCA43 | CN11 | 1 | CKCA43X7R1C104M | ? | ? | ? | ?
CAPN4I-100NF,16V,X7R,CKCA43 | CN10 | 1 | CKCA43X7R1C104M | ? | ? | ? | ?
CAPN4I-100NF,16V,X7R,CKCA43 | CN9 | 1 | CKCA43X7R1C104M | ? | ? | ? | ?
CAPN4I-100NF,16V,X7R,CKCA43 | CN8 | 1 | CKCA43X7R1C104M | ? | ? | ? | ?
CAPN4I-100NF,16V,X7R,CKCA43 | CN7 | 1 | CKCA43X7R1C104M | ? | ? | ? | ?
CAPN4I-100NF,16V,X7R,CKCA43 | CN6 | 1 | CKCA43X7R1C104M | ? | ? | ? | ?
CAPN4I-100NF,16V,X7R,CKCA43 | CN5 | 1 | CKCA43X7R1C104M | ? | ? | ? | ?
CAPN4I-100NF,16V,X7R,CKCA43 | CN4 | 1 | CKCA43X7R1C104M | ? | ? | ? | ?
CAPN4I-100NF,16V,X7R,CKCA43 | CN3 | 1 | CKCA43X7R1C104M | ? | ? | ? | ?
CAPN4I-100NF,16V,X7R,CKCA43 | CN2 | 1 | CKCA43X7R1C104M | ? | ? | ? | ?
CAPN4I-100NF,16V,X7R,CKCA43 | CN1 | 1 | CKCA43X7R1C104M | ? | ? | ? | ?
COAX-PLEMO00D | PX62 | 1 | EPA.00.250.NTN | ? | ? | ? | ?
COAX-PLEMO00D | PX61 | 1 | EPA.00.250.NTN | ? | ? | ? | ?
COAX-PLEMO00D | PX54 | 1 | EPA.00.250.NTN | ? | ? | ? | ?
COAX-PLEMO00D | PX53 | 1 | EPA.00.250.NTN | ? | ? | ? | ?
COAX-PLEMO00D | PX64 | 1 | EPA.00.250.NTN | ? | ? | ? | ?
COAX-PLEMO00D | PX63 | 1 | EPA.00.250.NTN | ? | ? | ? | ?
COAX-PLEMO00D | PX56 | 1 | EPA.00.250.NTN | ? | ? | ? | ?
COAX-PLEMO00D | PX55 | 1 | EPA.00.250.NTN | ? | ? | ? | ?
COAX-PLEMO00D | PX58 | 1 | EPA.00.250.NTN | ? | ? | ? | ?
COAX-PLEMO00D | PX57 | 1 | EPA.00.250.NTN | ? | ? | ? | ?
COAX-PLEMO00D | PX50 | 1 | EPA.00.250.NTN | ? | ? | ? | ?
COAX-PLEMO00D | PX49 | 1 | EPA.00.250.NTN | ? | ? | ? | ?
COAX-PLEMO00D | PX60 | 1 | EPA.00.250.NTN | ? | ? | ? | ?
COAX-PLEMO00D | PX59 | 1 | EPA.00.250.NTN | ? | ? | ? | ?
COAX-PLEMO00D | PX52 | 1 | EPA.00.250.NTN | ? | ? | ? | ?
COAX-PLEMO00D | PX51 | 1 | EPA.00.250.NTN | ? | ? | ? | ?
COAX-PLEMO00D | PX46 | 1 | EPA.00.250.NTN | ? | ? | ? | ?
COAX-PLEMO00D | PX45 | 1 | EPA.00.250.NTN | ? | ? | ? | ?
COAX-PLEMO00D | PX38 | 1 | EPA.00.250.NTN | ? | ? | ? | ?
COAX-PLEMO00D | PX37 | 1 | EPA.00.250.NTN | ? | ? | ? | ?
COAX-PLEMO00D | PX48 | 1 | EPA.00.250.NTN | ? | ? | ? | ?
COAX-PLEMO00D | PX47 | 1 | EPA.00.250.NTN | ? | ? | ? | ?
COAX-PLEMO00D | PX40 | 1 | EPA.00.250.NTN | ? | ? | ? | ?
COAX-PLEMO00D | PX39 | 1 | EPA.00.250.NTN | ? | ? | ? | ?
COAX-PLEMO00D | PX42 | 1 | EPA.00.250.NTN | ? | ? | ? | ?
COAX-PLEMO00D | PX41 | 1 | EPA.00.250.NTN | ? | ? | ? | ?
COAX-PLEMO00D | PX34 | 1 | EPA.00.250.NTN | ? | ? | ? | ?
COAX-PLEMO00D | PX33 | 1 | EPA.00.250.NTN | ? | ? | ? | ?
COAX-PLEMO00D | PX44 | 1 | EPA.00.250.NTN | ? | ? | ? | ?
COAX-PLEMO00D | PX43 | 1 | EPA.00.250.NTN | ? | ? | ? | ?
COAX-PLEMO00D | PX36 | 1 | EPA.00.250.NTN | ? | ? | ? | ?
COAX-PLEMO00D | PX35 | 1 | EPA.00.250.NTN | ? | ? | ? | ?
COAX-PLEMO00D | PX30 | 1 | EPA.00.250.NTN | ? | ? | ? | ?
COAX-PLEMO00D | PX29 | 1 | EPA.00.250.NTN | ? | ? | ? | ?
COAX-PLEMO00D | PX22 | 1 | EPA.00.250.NTN | ? | ? | ? | ?
COAX-PLEMO00D | PX21 | 1 | EPA.00.250.NTN | ? | ? | ? | ?
COAX-PLEMO00D | PX32 | 1 | EPA.00.250.NTN | ? | ? | ? | ?
COAX-PLEMO00D | PX31 | 1 | EPA.00.250.NTN | ? | ? | ? | ?
COAX-PLEMO00D | PX24 | 1 | EPA.00.250.NTN | ? | ? | ? | ?
COAX-PLEMO00D | PX23 | 1 | EPA.00.250.NTN | ? | ? | ? | ?
COAX-PLEMO00D | PX26 | 1 | EPA.00.250.NTN | ? | ? | ? | ?
COAX-PLEMO00D | PX25 | 1 | EPA.00.250.NTN | ? | ? | ? | ?
COAX-PLEMO00D | PX18 | 1 | EPA.00.250.NTN | ? | ? | ? | ?
COAX-PLEMO00D | PX17 | 1 | EPA.00.250.NTN | ? | ? | ? | ?
COAX-PLEMO00D | PX28 | 1 | EPA.00.250.NTN | ? | ? | ? | ?
COAX-PLEMO00D | PX27 | 1 | EPA.00.250.NTN | ? | ? | ? | ?
COAX-PLEMO00D | PX20 | 1 | EPA.00.250.NTN | ? | ? | ? | ?
COAX-PLEMO00D | PX19 | 1 | EPA.00.250.NTN | ? | ? | ? | ?
COAX-PLEMO00D | PX14 | 1 | EPA.00.250.NTN | ? | ? | ? | ?
COAX-PLEMO00D | PX13 | 1 | EPA.00.250.NTN | ? | ? | ? | ?
COAX-PLEMO00D | PX6 | 1 | EPA.00.250.NTN | ? | ? | ? | ?
COAX-PLEMO00D | PX5 | 1 | EPA.00.250.NTN | ? | ? | ? | ?
COAX-PLEMO00D | PX16 | 1 | EPA.00.250.NTN | ? | ? | ? | ?
COAX-PLEMO00D | PX15 | 1 | EPA.00.250.NTN | ? | ? | ? | ?
COAX-PLEMO00D | PX8 | 1 | EPA.00.250.NTN | ? | ? | ? | ?
COAX-PLEMO00D | PX7 | 1 | EPA.00.250.NTN | ? | ? | ? | ?
COAX-PLEMO00D | PX10 | 1 | EPA.00.250.NTN | ? | ? | ? | ?
COAX-PLEMO00D | PX9 | 1 | EPA.00.250.NTN | ? | ? | ? | ?
COAX-PLEMO00D | PX2 | 1 | EPA.00.250.NTN | ? | ? | ? | ?
COAX-PLEMO00D | PX1 | 1 | EPA.00.250.NTN | ? | ? | ? | ?
COAX-PLEMO00D | PX12 | 1 | EPA.00.250.NTN | ? | ? | ? | ?
COAX-PLEMO00D | PX11 | 1 | EPA.00.250.NTN | ? | ? | ? | ?
COAX-PLEMO00D | PX4 | 1 | EPA.00.250.NTN | ? | ? | ? | ?
COAX-PLEMO00D | PX3 | 1 | EPA.00.250.NTN | ? | ? | ? | ?
CON150P-QSS75_01FDA | J1 | 1 | QSS-075-01-F-D-A | ? | ? | ? | ?
R4ISMD_1206-180 | RZ16 | 1 | 307-0141 | ? | ? | ? | ?
R4ISMD_1206-180 | RZ15 | 1 | 307-0141 | ? | ? | ? | ?
R4ISMD_1206-180 | RZ14 | 1 | 307-0141 | ? | ? | ? | ?
R4ISMD_1206-180 | RZ13 | 1 | 307-0141 | ? | ? | ? | ?
R4ISMD_1206-180 | RZ12 | 1 | 307-0141 | ? | ? | ? | ?
R4ISMD_1206-180 | RZ11 | 1 | 307-0141 | ? | ? | ? | ?
R4ISMD_1206-180 | RZ10 | 1 | 307-0141 | ? | ? | ? | ?
R4ISMD_1206-180 | RZ9 | 1 | 307-0141 | ? | ? | ? | ?
R4ISMD_1206-180 | RZ8 | 1 | 307-0141 | ? | ? | ? | ?
R4ISMD_1206-180 | RZ7 | 1 | 307-0141 | ? | ? | ? | ?
R4ISMD_1206-180 | RZ6 | 1 | 307-0141 | ? | ? | ? | ?
R4ISMD_1206-180 | RZ5 | 1 | 307-0141 | ? | ? | ? | ?
R4ISMD_1206-180 | RZ4 | 1 | 307-0141 | ? | ? | ? | ?
R4ISMD_1206-180 | RZ3 | 1 | 307-0141 | ? | ? | ? | ?
R4ISMD_1206-180 | RZ2 | 1 | 307-0141 | ? | ? | ? | ?
R4ISMD_1206-180 | RZ1 | 1 | 307-0141 | ? | ? | ? | ?
TVS_DIODE_ARRAY_SP3010_UDFN-SP3010-04UTG | D16 | 1 | SP3010-04UTG | ? | ? | ? | ?
TVS_DIODE_ARRAY_SP3010_UDFN-SP3010-04UTG | D15 | 1 | SP3010-04UTG | ? | ? | ? | ?
TVS_DIODE_ARRAY_SP3010_UDFN-SP3010-04UTG | D14 | 1 | SP3010-04UTG | ? | ? | ? | ?
TVS_DIODE_ARRAY_SP3010_UDFN-SP3010-04UTG | D13 | 1 | SP3010-04UTG | ? | ? | ? | ?
TVS_DIODE_ARRAY_SP3010_UDFN-SP3010-04UTG | D12 | 1 | SP3010-04UTG | ? | ? | ? | ?
TVS_DIODE_ARRAY_SP3010_UDFN-SP3010-04UTG | D11 | 1 | SP3010-04UTG | ? | ? | ? | ?
TVS_DIODE_ARRAY_SP3010_UDFN-SP3010-04UTG | D10 | 1 | SP3010-04UTG | ? | ? | ? | ?
TVS_DIODE_ARRAY_SP3010_UDFN-SP3010-04UTG | D9 | 1 | SP3010-04UTG | ? | ? | ? | ?
TVS_DIODE_ARRAY_SP3010_UDFN-SP3010-04UTG | D8 | 1 | SP3010-04UTG | ? | ? | ? | ?
TVS_DIODE_ARRAY_SP3010_UDFN-SP3010-04UTG | D7 | 1 | SP3010-04UTG | ? | ? | ? | ?
TVS_DIODE_ARRAY_SP3010_UDFN-SP3010-04UTG | D6 | 1 | SP3010-04UTG | ? | ? | ? | ?
TVS_DIODE_ARRAY_SP3010_UDFN-SP3010-04UTG | D5 | 1 | SP3010-04UTG | ? | ? | ? | ?
TVS_DIODE_ARRAY_SP3010_UDFN-SP3010-04UTG | D4 | 1 | SP3010-04UTG | ? | ? | ? | ?
TVS_DIODE_ARRAY_SP3010_UDFN-SP3010-04UTG | D3 | 1 | SP3010-04UTG | ? | ? | ? | ?
TVS_DIODE_ARRAY_SP3010_UDFN-SP3010-04UTG | D2 | 1 | SP3010-04UTG | ? | ? | ? | ?
TVS_DIODE_ARRAY_SP3010_UDFN-SP3010-04UTG | D1 | 1 | SP3010-04UTG | ? | ? | ? | ?
TOTAL |  | 113

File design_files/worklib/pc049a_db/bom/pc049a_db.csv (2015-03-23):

TITLE: Bill of Materials
DATE: 03/04/2015
DESIGN: pc049a_db
TEMPLATE: /projects/HEP_Instrumentation/cad/tools/cadence_templates/spreadsheet-format.bom
CALLOUT: bom.callouts
Part Name | Ref Des | Qty | PART_NUMBER | PART_DESCRIPTION | OL_COMMENTS | KL_COMMENTS | PL_COMMENTS
CAPN4I-100NF,16V,X7R,CKCA43 | CN1,CN2,CN3,CN4,CN5,CN6,CN7,CN8,CN9,CN10,CN11,CN12,CN13,CN14,CN15,CN16 | 16 | CKCA43X7R1C104M | ? | ? | ? | ?
COAX-PLEMO00D | PX1,PX2,PX3,PX4,PX5,PX6,PX7,PX8,PX9,PX10,PX11,PX12,PX13,PX14,PX15,PX16,PX17,PX18,PX19,PX20,PX21,PX22,PX23,PX24,PX25,PX26,PX27,PX28,PX29,PX30,PX31,PX32,PX33,PX34,PX35,PX36,PX37,PX38,PX39,PX40,PX41,PX42,PX43,PX44,PX45,PX46,PX47,PX48,PX49,PX50,PX51,PX52,PX53,PX54,PX55,PX56,PX57,PX58,PX59,PX60,PX61,PX62,PX63,PX64 | 64 | EPA.00.250.NTN | ? | ? | ? | ?
CON150P-QSS75_01FDA | J1 | 1 | QSS-075-01-F-D-A | ? | ? | ? | ?
R4ISMD_1206-180 | RZ1,RZ2,RZ3,RZ4,RZ5,RZ6,RZ7,RZ8,RZ9,RZ10,RZ11,RZ12,RZ13,RZ14,RZ15,RZ16 | 16 | 307-0141 | ? | ? | ? | ?
TVS_DIODE_ARRAY_SP3010_UDFN-SP3010-04UTG | D1,D2,D3,D4,D5,D6,D7,D8,D9,D10,D11,D12,D13,D14,D15,D16 | 16 | SP3010-04UTG | ? | ? | ? | ?
TOTAL |  | 113

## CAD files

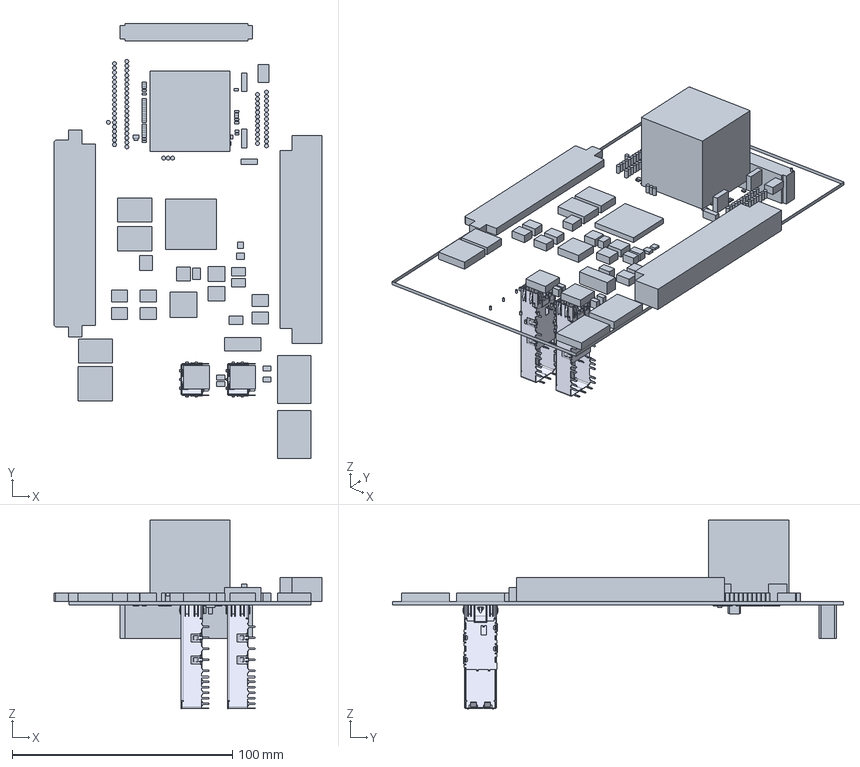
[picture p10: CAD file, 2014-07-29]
design_files/worklib/pc049a_toplevel/physical/pc049a_toplevel_05_dummy_tst.stp
121.6 x 205.0 x 85.8 mm
BOARD
SOT23
SOT23-5
SAMTEC_TSW-103-23-L-S
CON14MD_2MM
OSCSC254P490X696X180-6N
SOP65P490X110-8N
FGA456
OSC_4PIN_53S
SOIC127P1032X265-16N
QFN50P500X500X100-33N-S355
OSC_SILABS_SI570
c-1489779-01-c-3d_2 x 2
QFN50P400X500X80-29N-R375X275
TO254P1435X460-4N x 2
MURATA_BNX02
INDC2012X90N x 4
TYCO_1367073 x 2
MOLEX_47082-001 x 2
LGA133S127P12X12_05-08-1766
SOP65P490X95-8N x 2
CON150_QTSDA
HARTING_0903196X921
HARTING_09732966801
SAMTEC_SSW-103-01-G-D
CONHE13D3X1M x 2
C3216POL
SOIC127P600X175-8N x 7
PQFP240_050
C0603 x 4
C0402 x 88
SOD323_INV
1-HOLE_0-8P x 68

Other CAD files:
design_files/worklib/pc049a_db/physical/pc049a_lemo_db_05.dxf

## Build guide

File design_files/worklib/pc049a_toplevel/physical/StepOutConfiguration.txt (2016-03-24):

EXPORT_UNIT = Millimeter
EXPORT_PROTOCOL = 214
BARE_BOARD_ONLY = NO
MAPPED_PACKAGE = NO
UNMAPPED_PACKAGE = YES
EXTERNAL_COPPER = NO
MECH_PART = NO
MECH_DRILL = YES
ZIP_FILE = NO

SOURCE_ID = allegro_16.6S014

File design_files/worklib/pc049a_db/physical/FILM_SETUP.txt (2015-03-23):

(axlfcreate "PASTEMASK_BOTTOM" '(0 0 0 0 25400 1 0 0 0 0 0 1 1)
	'("PIN/PASTEMASK_BOTTOM" "PACKAGE GEOMETRY/PASTEMASK_BOTTOM" ))
(axlfcreate "ASSEMBLY_BOTTOM" '(0 0 0 2000 25400 1 0 0 0 0 0 1 1)
	'("REF DES/ASSEMBLY_BOTTOM" "PACKAGE GEOMETRY/ASSEMBLY_BOTTOM" "DRAWING FORMAT/OUTLINE" "DRAWING FORMAT/TITLE_BLOCK" "DRAWING FORMAT/TITLE_DATA" "DRAWING FORMAT/REVISION_BLOCK" "DRAWING FORMAT/REVISION_DATA" "BOARD GEOMETRY/OUTLINE" "BOARD GEOMETRY/DIMENSION" ))
(axlfcreate "SOLDERMASK_TOP" '(0 0 0 0 25400 1 0 0 0 0 0 1 1)
	'("PIN/SOLDERMASK_TOP" "PACKAGE GEOMETRY/SOLDERMASK_TOP" "BOARD GEOMETRY/SOLDERMASK_TOP" ))
(axlfcreate "SOLDERMASK_BOTTOM" '(0 0 0 0 25400 1 0 0 0 0 0 1 1)
	'("PIN/SOLDERMASK_BOTTOM" "PACKAGE GEOMETRY/SOLDERMASK_BOTTOM" "BOARD GEOMETRY/SOLDERMASK_BOTTOM" ))
(axlfcreate "SILKSCREEN_TOP" '(0 0 0 2500 25400 1 0 0 0 0 0 1 1)
	'("REF DES/SILKSCREEN_TOP" "BOARD GEOMETRY/SILKSCREEN_TOP" ))
(axlfcreate "SILKSCREEN_BOTTOM" '(0 0 0 2500 25400 1 0 0 0 0 0 1 1)
	'("REF DES/SILKSCREEN_BOTTOM" "BOARD GEOMETRY/SILKSCREEN_BOTTOM" ))
(axlfcreate "DRILL_FIGURE" '(0 0 0 5000 25400 1 0 0 0 0 0 1 0)
	'("MANUFACTURING/NCDRILL_LEGEND" "MANUFACTURING/NCDRILL_FIGURE" "MANUFACTURING/NCLEGEND-1-6" "DRAWING FORMAT/OUTLINE" "DRAWING FORMAT/TITLE_BLOCK" "DRAWING FORMAT/TITLE_DATA" "DRAWING FORMAT/REVISION_BLOCK" "DRAWING FORMAT/REVISION_DATA" "BOARD GEOMETRY/OUTLINE" ))
(axlfcreate "OUTLINE" '(0 0 0 1000 25400 1 0 0 0 0 0 1 1)
	'("BOARD GEOMETRY/OUTLINE" ))
(axlfcreate "PASTEMASK_TOP" '(0 0 0 0 25400 1 0 0 0 0 0 1 1)
	'("PIN/PASTEMASK_TOP" "PACKAGE GEOMETRY/PASTEMASK_TOP" ))
(axlfcreate "ASSEMBLY_TOP" '(0 0 0 2000 25400 1 0 0 0 0 0 1 1)
	'("REF DES/ASSEMBLY_TOP" "PACKAGE GEOMETRY/ASSEMBLY_TOP" "DRAWING FORMAT/OUTLINE" "DRAWING FORMAT/TITLE_BLOCK" "DRAWING FORMAT/TITLE_DATA" "DRAWING FORMAT/REVISION_BLOCK" "DRAWING FORMAT/REVISION_DATA" "BOARD GEOMETRY/OUTLINE" "BOARD GEOMETRY/DIMENSION" ))
(axlfcreate "BOTTOM" '(0 0 0 0 25400 1 0 0 0 0 0 1 1)
	'("ETCH/BOTTOM" "PIN/BOTTOM" "VIA CLASS/BOTTOM" ))
	'("ETCH/L2" "PIN/L2" "VIA CLASS/L2" ))
(axlfcreate "TOP" '(0 0 0 0 25400 1 0 0 0 0 0 1 1)
	'("ETCH/TOP" "PIN/TOP" "VIA CLASS/TOP" ))

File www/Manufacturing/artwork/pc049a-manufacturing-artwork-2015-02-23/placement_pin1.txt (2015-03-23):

UUNITS = MILLIMETERS
SFP1                 19.0000        0.0000       90    TYCO_6367034-1      
SFP3                 0.0000         0.0000       90    TYCO_6367034-1      
SFP2                 21.3300       37.1000       90    TYCO_6367035-1      
SFP4                 2.3300        37.1000       90    TYCO_6367035-1      
IC16                 53.5250      119.4410      270    SOT23_5             
R79                  84.2010       66.6640       90    C0805               
R80                  1.2250        64.9000        0    C0805               
C138                 42.8500      117.6200      270    C0402               
IC21                 -4.8750      152.9000        0    SOT223_5            
R49                  38.9290      130.0970       90    C0603               
R66                  38.9300      127.1800       90    C0603               
R68                  -6.5120      154.6770      180  m C0603               
IC20                 35.1250      131.4000      270    SC70                
REG3                 68.5140      110.2610        0    TO254P1435X460-4N   
U3                   39.4420      102.8530       90    BGA484C100P22X22_2300X2300X260
U5                   44.5046       81.2202      180    SOT23-5             
J4                   4.2510        90.1620        0    SK_SATA_SMD_STR     
J5                   4.2510       110.1620        0    SK_SATA_SMD_STR     
U4                   71.9420       78.8530       90    SOIC8               
RG1_1                51.7900      159.3760       90  m SOT223_4            
R77                  72.5040      135.5830      180    C0402               
R75                  49.9500      116.9400       90    C0603               
R76                  48.3700      118.4300      270    C0603               
IC22                 73.3390      125.0110      180    SOIC127P1030X265-16N
C163                 72.2080       22.3576       90  m C0603               
C164                 72.3604       45.2938       90  m C0603               
C165                 71.7080       -0.4020       90  m C0603               
R11                  70.2014        1.1232       90  m C0603               
J9                   87.1250       10.9000      180    CON2MC_508          
R71                  94.7124       31.8064      270    C0603               
IC5                  72.0920       66.4480      180    SOIC127P600X175-8N  
IC6                  72.0920       72.9480      180    SOIC127P600X175-8N  
IC7                  76.2920       82.7580        0    SOIC127P600X175-8N  
IC2                  81.5920       66.4480      180    SOIC127P600X175-8N  
IC3                  81.5920       72.9480      180    SOIC127P600X175-8N  
REG1                 39.5920       16.0450        0    TO254P1435X460-4N   
C115                 16.8440      107.4090      270    C1206               
C116                 23.9320      102.0990      180    C1206               
C126                 41.9300       85.5200       90    C1206               
C133                 20.0430      110.6080        0    C1206               
C136                 33.3540      120.9980      270    C1206               
C139                 58.0950       88.8910      180    C1206               
C142                 19.9420       91.8530        0    C1206               
C96                  66.2710      103.1150        0    C1206               
C97                  63.7070      104.6630       90    C1206               
R69                  -1.8130      154.6770      180  m C0603               
C127                 39.4420       91.9030      270  m C0402               
C145                 39.4500       99.7550       90  m C0402               
C148                 36.4100      100.7700        0  m C0402               
C151                 55.9120       97.5740        0  m C0402               
C153                 29.6020      113.7830      180  m C0402               
C155                 46.3920      101.8530        0  m C0402               
C157                 42.4420       95.9030      270  m C0402               
C117                 42.4290      105.9090      180  m C0402               
C118                 39.4420      100.9030      270  m C0402               
C119                 39.4500      105.8510       90  m C0402               
R64                  45.4600      117.6200      270    C0402               
R65                  44.4500      117.6100      270    C0402               
C101                 67.5750      111.7510        0    C0402               
C3                   16.5550       83.9320        0    C0402               
C9                   4.8290        45.0010        0    C0402               
C10                  4.8290        46.0170        0    C0402               
C12                  10.8090       39.7940      180    C0402               
C24                  22.4130       46.1060        0    C0402               
C25                  22.4130       45.1060        0    C0402               
C27                  28.3350       40.9370      180    C0402               
C59                  49.9420       82.8030      270    C0402               
C71                  22.9340      124.8810      180    C0402               
C107                 30.4910      102.8610      180  m C0402               
C110                 30.4910       98.7970      180  m C0402               
C51                  53.8350       70.6630      270    C0805               
C52                  52.9420       81.2530      270    C0805               
C53                  54.9420       81.2530      270    C0805               
C54                  59.9420       81.2530      270    C0805               
C55                  61.9420       81.2530      270    C0805               
C65                  23.8840      126.3810      180    C0805               
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
LD7                  94.7886       24.8588       90    D1206               
LD6                  25.4320       79.4480      270    D1206               
LD4                  16.4320       79.4480      270    D1206               
LD3                  19.4320       79.4480      270    D1206               
RN1                  17.6150       59.6450      270    ARC241_SO8          
RN2                  4.1150        59.6450      270    ARC241_SO8          
RZ1                  17.9400       71.1940        0    ARC241_SO8          
RZ2                  29.7020       79.2180        0    ARC241_SO8          
R63                  55.1920       94.8530        0    C0603               
R61                  54.9560      115.3070        0    C0603               
R48                  33.3410      131.5970      270    C0603               
R67                  -3.3610      152.8990        0  m C0603               
R7                   66.6240      115.7630      180    C0603               
R56                  45.9420       88.6030      270    C0603               
R57                  38.8150       62.5900       90  m C0603               
R58                  47.4510       62.5900       90  m C0603               
R59                  44.4420       88.6030      270    C0603               
R60                  55.1920       93.3530        0    C0603               
R62                  55.1900       96.3700        0    C0603               
SW3                  29.2970       68.4020       90    SW_TYCO_1571983-4   
SW1                  42.8470       61.8110       90    OMRON_B3SN-3012     
SW2                  51.4830       61.8110       90    OMRON_B3SN-3012     
SW4                  64.5670       98.9180       90    OMRON_B3SN-3012     
R53                  35.4200      102.1200      270  m C0603               
IC15                 38.3170       68.0350       90    SON50P300X200X100-9N-R175X155
J10                  14.2390       54.7550       90    SAMTEC_TSM-106-01-X-DV
LD2                  22.4320       79.4480      270    D1206               
LD5                  13.4320       79.4480      270    D1206               
LD1                  58.4020      120.8370      270    D1206               
R70                  25.4320       72.6980       90    C0603               
R52                  60.9130      121.0100      270    C0603               
R50                  17.0050       87.6820      270    C0603               
C34                  79.7398        0.5764        0  m C0603               
C88                  80.2906       46.2504        0  m C0603               
J1                   70.7450      198.9860      270  m CON150_QTSDA        
R44                  70.7602       46.7924       90  m C0603               
R51                  20.2550       87.9320      180    C0603               
R46                  66.1200      111.7390      270    C0603               
R47                  64.6600      110.2400      180    C0603               
U2                   20.7496       83.9922      180    SOT23-5             
R32                  29.0570       84.7100        0  m C0603               
R34                  27.8070       86.4600      270  m C0603               
R26                  35.9380       84.7100        0  m C0603               
R28                  34.4380       83.2100        0  m C0603               
R30                  32.0570       84.7100        0  m C0603               
R33                  29.3070       86.4600      270  m C0603               
R35                  25.8070       87.9600      270  m C0603               
R3                   37.4060       83.1760        0  m C0603               
R25                  35.6880       86.4600      270  m C0603               
R27                  34.1880       86.4600      270  m C0603               
R29                  32.6880       86.4600      270  m C0603               
R31                  30.8070       86.4600      270  m C0603               
QZ1                  36.8760       74.3480        0    OSC_SILABS_SI570    
IC1                  58.8330       71.6190        0    SOP65P490X95-8N     
IC9                  58.8330       76.6190        0    SOP65P490X95-8N     
J8                   23.9480      142.0290      270    CON14MD_2MM         
L5                   56.6920       81.3530        0    C0603               
L6                   61.9420       83.1030       90    C0603               
L7                   48.4420       81.6030       90    C0603               
L8                   25.4960      123.2380        0    C0603               
Z1                   55.4460       70.7028        0    SOT23               
QZ2                  45.8720       72.3270        0    OSCSC254P490X696X180-6N
U1                   46.1480       75.9940       90    OSC_4PIN_53S        
R54                  55.3110      110.8530      180    C0603               
R55                  51.7600      118.4300      270    C0603               
R20                  20.4000      120.0600       90    C0603               
R21                  14.3000      120.0600       90    C0603               
R14                  55.3450       72.3060      180    C0603               
R15                  51.4000       74.2860        0    C0603               
R16                  55.1150       74.5920        0    C0603               
R17                  50.6540       67.2260        0  m C0603               
IC11                 14.6110      127.9800        0    QFN50P500X500X100-33N-S355
LC1                  56.0306       -1.2950      180    MURATA_BNX02        
LC3                  57.7324       44.1202      180    MURATA_BNX02        
LC2                  57.5800       23.3430      180    MURATA_BNX02        
C44                  9.2820       102.6070        0    C0402               
C103                 73.9390      122.9560      180    C0603               
C100                 36.4320       70.7850      270    C0603               
C31                  35.6400       87.9900      270    C0603               
C48_1                54.1550      153.2895      270  m C0603               
C52_1                61.5256      146.4027      270  m C0603               
C53_1                19.4830      150.3896      180  m C0603               
C54_1                50.1699      151.2392      180  m C0603               
C48                  19.5100       97.7900       90    C0603               
C41                  41.3470        1.5550      270    C0603               
C95                  43.0488       46.9448      270    C0603               
C84                  41.2896       23.3510        0    C0603               
C42                  14.1570      104.4370      180    C0603               
C46                  17.9870       97.7930       90    C0603               
C13                  11.1090       42.0800      180    C0603               
C23                  6.0530        42.0800        0    C0603               
C28                  28.6350       42.2070      180    C0603               
C30                  23.5790       42.2070        0    C0603               
C47                  19.3100      101.1500      180    C0603               
C33                  81.8518        6.9660      180    CAPC3225X279N       
C35                  81.8360       10.4316      180    CAPC3225X279N       
C36                  81.8574        3.4302      180    CAPC3225X279N       
C37                  81.8614       -0.0586      180    CAPC3225X279N       
C87                  82.4056       52.6154      180    CAPC3225X279N       
C89                  82.4056       56.1154      180    CAPC3225X279N       
C90                  82.4056       45.6154      180    CAPC3225X279N       
C91                  82.4056       49.1154      180    CAPC3225X279N       
C76                  82.2424       33.1900      180    CAPC3225X279N       
C78                  82.2678       29.6848      180    CAPC3225X279N       
C79                  82.2678       26.1796      180    CAPC3225X279N       
C80                  82.2678       22.6744      180    CAPC3225X279N       
C38                  69.4100       13.4300      180    C1210               
C39                  69.4100       16.6400      180    C1210               
C92                  69.3300       62.3100      180    C1210               
C93                  69.3300       59.0900      180    C1210               
C81                  69.1700       36.2800      180    C1210               
C82                  69.1700       39.4800      180    C1210               
J6                   3.7300        26.8000       90    TYCO_1367073        
J7                   22.7300       26.8000       90    TYCO_1367073        
IC13                 68.0580      117.5590      180    SOP65P490X110-8N    
C32                  75.3576       14.9528        0    C7343POL            
C86                  75.9056       60.6154        0    C7343POL            
C75                  75.7386       37.6858        0    C7343POL            
C40                  63.1816       14.7726      180    POSCAP_D3           
C94                  63.4530       60.4430      180    POSCAP_D3           
C83                  63.4102       37.5056      180    POSCAP_D3           
C85                  10.6210       94.0980        0    POSCAP_D3           
L9                   23.3420      104.3530      180    INDC2012X90N        
L1                   9.7240        45.7740      270    INDC2012X90N        
L2                   7.4380        43.9740       90    INDC2012X90N        
L3                   27.2500       45.9010      270    INDC2012X90N        
L4                   24.9640       44.1010       90    INDC2012X90N        
RG1                  11.9912      101.7674        0    QFN50P400X500X80-29N-R375X275
IC10                 68.9314        3.6244      270    LGA133S127P12X12_05-08-1766
IC14                 69.4902       49.2936      270    LGA133S127P12X12_05-08-1766
IC4                  69.3378       26.3574      270    LGA133S127P12X12_05-08-1766
R13                  10.1820      101.5910      180    C0402               
R72                  66.8940       20.0570      180  m C0603               
R73                  67.0210       43.0440      180  m C0603               
R74                  66.3860       -2.6760      180  m C0603               
R10                  75.8910        2.3932       90  m C0603               
R43                  76.4498       48.0624       90  m C0603               
R38                  76.2974       25.1262       90  m C0603               
R12                  80.5526       -2.8272      180    C0603               
R45                  81.1114       42.8420      180    C0603               
R40                  80.9590       19.9058      180    C0603               
R18                  20.6500      132.1400      270    C0603               
R19                  17.3400      120.0600       90    C0603               
R22                  19.1220      132.1110      270    C0603               
R23                  18.8680      120.0700       90    C0603               
R24                  15.8200      120.0700       90    C0603               
R8                   76.7600       -1.3000        0  m C0603               
R9                   75.2760       -2.8030      180  m C0603               
R41                  77.2840       44.4410        0  m C0603               
R42                  75.7840       42.9170      180  m C0603               
R36                  77.1744       21.5060        0  m C0603               
R37                  75.6800       20.0000      180  m C0603               
R39                  70.6078       23.8562       90  m C0603               
LK1                  60.1684       21.3028        0    1-HOLE_0-8P         
LK2                  60.2954       44.2390        0    1-HOLE_0-8P         
LK3                  65.8660      107.6870        0    1-HOLE_0-8P         
LK4                  19.5900      104.6700        0    1-HOLE_0-8P         
LK5                  63.7070      102.9880        0    1-HOLE_0-8P         
LK6                  43.1330      130.4200        0    1-HOLE_0-8P         
LK7                  36.2750       11.2940        0    1-HOLE_0-8P         
LK8                  -1.5790      147.7440        0    1-HOLE_0-8P         
LK9                  -5.3890      147.8710        0    1-HOLE_0-8P         
LK1_1                79.5470      148.2455        0    1-HOLE_0-8P         
LK2_1                16.0470      149.7695        0    1-HOLE_0-8P         
LK3_1                10.4590      173.1375        0    1-HOLE_0-8P         
LK4_1                79.5470      170.5975        0    1-HOLE_0-8P         
LK5_1                79.5470      166.5335        0    1-HOLE_0-8P         
LK6_1                75.4830      169.5815        0    1-HOLE_0-8P         
LK7_1                75.4830      165.5175        0    1-HOLE_0-8P         
LK8_1                10.4590      175.1695        0    1-HOLE_0-8P         
LK9_1                79.5470      164.5015        0    1-HOLE_0-8P         
LK10_1               75.4830      161.4535        0    1-HOLE_0-8P         
LK11_1               10.4590      162.9775        0    1-HOLE_0-8P         
LK12_1               16.0470      155.8655        0    1-HOLE_0-8P         
LK13_1               79.5470      156.3735        0    1-HOLE_0-8P         
LK14_1               10.4590      152.8175        0    1-HOLE_0-8P         
LK15_1               16.0470      147.7375        0    1-HOLE_0-8P         
LK16_1               16.0470      178.2175        0    1-HOLE_0-8P         
LK17_1               10.4590      154.8495        0    1-HOLE_0-8P         
LK18_1               16.0470      176.1855        0    1-HOLE_0-8P         
LK19_1               16.0470      157.8975        0    1-HOLE_0-8P         
LK20_1               16.0470      163.9935        0    1-HOLE_0-8P         
LK21_1               75.4830      159.4215        0    1-HOLE_0-8P         
LK22_1               10.4590      167.0415        0    1-HOLE_0-8P         
LK23_1               79.5470      154.3415        0    1-HOLE_0-8P         
LK24_1               10.4590      158.9135        0    1-HOLE_0-8P         
LK25_1               16.0470      161.9615        0    1-HOLE_0-8P         
LK26_1               66.8470      144.1035        0    1-HOLE_0-8P         
LK27_1               10.4590      156.8815        0    1-HOLE_0-8P         
LK28_1               79.5470      152.3095        0    1-HOLE_0-8P         
LK29_1               75.4830      151.2935        0    1-HOLE_0-8P         
LK30_1               7.6650       156.8815        0    1-HOLE_0-8P         
LK31_1               10.4590      179.4875        0    1-HOLE_0-8P         
LK32_1               16.0470      166.0255        0    1-HOLE_0-8P         
LK33_1               16.0470      151.8015        0    1-HOLE_0-8P         
LK34_1               79.5470      160.4375        0    1-HOLE_0-8P         
LK35_1               16.0470      182.5355        0    1-HOLE_0-8P         
LK36_1               10.4590      160.9455        0    1-HOLE_0-8P         
LK37_1               10.4590      146.7215        0    1-HOLE_0-8P         
LK38_1               79.5470      162.4695        0    1-HOLE_0-8P         
LK39_1               10.4590      181.5195        0    1-HOLE_0-8P         
LK40_1               75.4830      155.3575        0    1-HOLE_0-8P         
LK41_1               79.5470      168.5655        0    1-HOLE_0-8P         
LK42_1               10.4590      177.2015        0    1-HOLE_0-8P         
LK43_1               16.0470      168.0575        0    1-HOLE_0-8P         
LK44_1               10.4590      150.7855        0    1-HOLE_0-8P         
LK45_1               79.5470      158.4055        0    1-HOLE_0-8P         
LK46_1               75.4830      167.5495        0    1-HOLE_0-8P         
LK47_1               16.0470      145.7055        0    1-HOLE_0-8P         
LK48_1               16.0470      153.8335        0    1-HOLE_0-8P         
LK49_1               75.4830      157.3895        0    1-HOLE_0-8P         
LK50_1               16.0470      159.9295        0    1-HOLE_0-8P         
LK51_1               75.4830      149.2615        0    1-HOLE_0-8P         
LK52_1               79.5470      150.2775        0    1-HOLE_0-8P         
LK53_1               16.0470      170.0895        0    1-HOLE_0-8P         
LK54_1               32.8110      140.6255        0    1-HOLE_0-8P         
LK55_1               34.8430      138.4665        0    1-HOLE_0-8P         
LK56_1               36.8750      140.6255        0    1-HOLE_0-8P         
LK57_1               16.0470      180.5035        0    1-HOLE_0-8P         
LK58_1               75.4830      163.4855        0    1-HOLE_0-8P         
LK59_1               10.4590      148.7535        0    1-HOLE_0-8P         
LK60_1               16.0470      184.5675        0    1-HOLE_0-8P         
LK61_1               16.0470      174.1535        0    1-HOLE_0-8P         
LK62_1               10.4590      171.1055        0    1-HOLE_0-8P         
LK63_1               75.4830      153.3255        0    1-HOLE_0-8P         
LK64_1               16.0470      172.1215        0    1-HOLE_0-8P         
LK65_1               10.4590      169.0735        0    1-HOLE_0-8P         
LK66_1               10.4590      183.5515        0    1-HOLE_0-8P         
LK67_1               10.4590      165.0095        0    1-HOLE_0-8P         
LK68_1               75.4830      147.2295        0    1-HOLE_0-8P         
C49                  12.3330      128.8210      180    C0402               
C1                   64.1650      117.5410        0  m C0402               
C2                   76.8920       70.3530        0  m C0402               
C4                   73.5470      126.2810        0  m C0402               
C5                   80.9920       82.8530      180  m C0402               
C6                   67.3920       72.8530        0  m C0402               
C7                   71.3850       83.9380      180  m C0402               
C8                   66.8920       78.8530        0  m C0402               
C14                  34.9420       77.9030       90    C0402               
C15                  12.3400      124.7400      180    C0402               
C16                  8.2660        88.8910        0    C0402               
C17                  8.3930       104.1310        0    C0402               
C18                  8.2660        87.8750        0    C0402               
C19                  12.3330      127.8050      180    C0402               
C20                  8.3010       105.1620        0    C0402               
C21                  12.3330      125.7730      180    C0402               
C45                  9.2820       100.5750        0    C0402               
C60                  49.2000       75.9890      180  m C0402               
C61                  16.8360      120.7510      270  m C0402               
C77                  79.8462       23.3094        0  m C0402               
C128                 17.4420       65.9030       90    C0402               
C130                 47.4510       87.4250      270  m C0402               
C131                 11.5760       45.1730       90    C0402               
C132                 28.9420       45.3000       90    C0402               
C134                 32.4420      106.9030      270  m C0402               
C137                 42.4920      102.8530      180  m C0402               
C140                 40.4500      107.7560       90  m C0402               
C141                 39.8310       88.3140      270  m C0402               
C143                 44.3450      113.7830        0  m C0402               
C144                 31.9570      116.0110       90  m C0402               
C146                 50.4610       92.9880      270  m C0402               
C147                 34.7510      116.0110       90  m C0402               
C149                 23.3790      102.0990      180  m C0402               
C150                 22.3630       89.6530        0    C0402               
C152                 50.3630      102.8690        0  m C0402               
C154                 32.4920      102.8530      180  m C0402               
C156                 37.6030      113.7830      180  m C0402               
C158                 26.1150       95.8180       90  m C0402               
C159                 55.0200      109.3680      180    C0402               
C160                 40.4660      108.8880      270  m C0402               
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
J3_1                 69.3870      152.0555      270    CONHE13D3X1M        
J4_1                 69.3870      177.7095      270    CONHE13D3X1M        
J1_1                 76.9850      176.4995      270    SAMTEC_SSW-103-01-G-D
J2                   95.3650      139.7200        0    HARTING_0903196X921 
J3                   -9.1150       50.8200      180    HARTING_09732966801 
D1_1                 52.8550      148.7395        0  m SOD323_INV          
U1_1                 59.4950      178.9795      270    PQFP240_050         
R20_1                33.0450      157.6995      180  m C0402               
R21_1                35.9450      157.6995        0  m C0402               
R22_1                33.0450      159.6995      180  m C0402               
R23_1                35.9450      159.6995        0  m C0402               
R25_1                31.0324      165.1165      180  m C0402               
R26_1                23.5450      165.1995      180  m C0402               
R28_1                33.9450      162.6995        0  m C0402               
R29_1                35.9450      162.6995        0  m C0402               
R30_1                24.4450      161.1995        0  m C0402               
R31_1                23.5450      162.1995      180  m C0402               
R32_1                31.0476      153.2569      180  m C0402               
R33_1                31.9476      152.0109        0  m C0402               
R34_1                54.4450      171.6995        0  m C0402               
R35_1                53.5450      170.6995      180  m C0402               
R36_1                31.0246      147.7191      180  m C0402               
R37_1                23.5443      148.1433      180  m C0402               
R14_1                35.0625      161.6673      180  m C0402               
R17_1                55.9450      158.6995        0  m C0402               
R78                  14.1400      130.7600        0    C0402               
R1                   81.9420       68.8030       90  m C0402               
R2                   81.9420       75.3030       90  m C0402               
R6                   72.5970       79.9430       90  m C0402               
R24_1                63.7990      150.7275      270    C0402               
R3_1                 58.7835      147.9388        0  m C0402               
R4_1                 23.5443      150.5662      180  m C0402               
R5_1                 31.0476      163.9055      180  m C0402               
R6_1                 56.8478      174.7564        0  m C0402               
R7_1                 55.9450      169.1995        0  m C0402               
R8_1                 31.0450      173.6995      180  m C0402               
R9_1                 55.9353      167.8937        0  m C0402               
R10_1                32.9763      167.1576      180  m C0402               
R11_1                55.9864      166.0878        0  m C0402               
R12_1                24.4450      157.1995        0  m C0402               
R13_1                55.9450      161.6995        0  m C0402               
R15_1                24.4450      154.6995        0  m C0402               
R16_1                24.4450      152.6995        0  m C0402               
R27_1                34.0050      151.3895      180  m C0402               
R46_1                62.9743      146.7405      270  m C0402               
R47_1                19.7509      149.0089      180  m C0402               
R4                   72.2850       82.6680        0  m C0402               
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

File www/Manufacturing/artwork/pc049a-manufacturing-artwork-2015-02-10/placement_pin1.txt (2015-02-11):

UUNITS = MILLIMETERS
SFP1                 19.0000        0.0000       90    TYCO_6367034-1      
SFP3                 0.0000         0.0000       90    TYCO_6367034-1      
SFP2                 21.3300       37.1000       90    TYCO_6367035-1      
SFP4                 2.3300        37.1000       90    TYCO_6367035-1      
IC16                 53.5250      119.4410      270    SOT23_5             
R79                  84.6620       66.5280       90    C0805               
R80                  1.2250        64.9000        0    C0805               
C138                 42.8790      117.5350      270    C0402               
IC21                 -4.8750      152.9000        0    SOT223_5            
R49                  38.9290      130.0970       90    C0603               
R66                  38.9290      127.3030       90    C0603               
R68                  -6.5120      154.6770      180  m C0603               
IC20                 35.1250      131.4000      270    SC70                
REG3                 68.5140      110.2610        0    TO254P1435X460-4N   
U3                   39.4420      102.8530       90    BGA484C100P22X22_2300X2300X260
U5                   44.5046       81.2202      180    SOT23-5             
J4                   4.2510        90.1620        0    SK_SATA_SMD_STR     
J5                   4.2510       110.1620        0    SK_SATA_SMD_STR     
U4                   71.9420       78.8530       90    SOIC8               
RG1_1                51.7900      159.3760       90  m SOT223_4            
R77                  72.5040      135.5830      180    C0402               
R75                  49.9420      116.8330       90    C0603               
R76                  48.4420      118.3330      270    C0603               
IC22                 73.3390      125.0110      180    SOIC127P1030X265-16N
C163                 72.2080       22.3576       90  m C0603               
C164                 72.3604       45.2938       90  m C0603               
C165                 71.7080       -0.4020       90  m C0603               
R11                  70.2014        1.1232       90  m C0603               
J9                   87.1250       10.9000      180    CON2MC_508          
R71                  94.7124       31.8064      270    C0603               
IC5                  72.0920       66.4480      180    SOIC127P600X175-8N  
IC6                  72.0920       72.9480      180    SOIC127P600X175-8N  
IC7                  76.2920       82.7580        0    SOIC127P600X175-8N  
IC2                  81.5920       66.4480      180    SOIC127P600X175-8N  
IC3                  81.5920       72.9480      180    SOIC127P600X175-8N  
REG1                 39.5920       16.0450        0    TO254P1435X460-4N   
C115                 16.8440      107.4090      270    C1206               
C116                 23.9320      102.0990      180    C1206               
C126                 41.9420       85.8530       90    C1206               
C133                 20.0430      110.6080        0    C1206               
C136                 33.3540      120.9980      270    C1206               
C139                 58.0950       88.8910      180    C1206               
C142                 19.9420       91.8530        0    C1206               
C96                  66.2710      103.1150        0    C1206               
C97                  63.7070      104.6630       90    C1206               
R69                  -1.8130      154.6770      180  m C0603               
C127                 39.4420       91.9030      270  m C0402               
C145                 39.4500       99.7550       90  m C0402               
C148                 36.4710      100.8290        0  m C0402               
C151                 55.9120       97.5740        0  m C0402               
C153                 29.6020      113.7830      180  m C0402               
C155                 46.3920      101.8530        0  m C0402               
C157                 42.4420       95.9030      270  m C0402               
C117                 42.4290      105.9090      180  m C0402               
C118                 39.4420      100.9030      270  m C0402               
C119                 39.4500      105.8510       90  m C0402               
R64                  45.4420      117.5650      270    C0402               
R65                  44.4420      117.5650      270    C0402               
C101                 67.5750      111.7510        0    C0402               
C3                   16.5550       83.9320        0    C0402               
C9                   4.8290        45.0010        0    C0402               
C10                  4.8290        46.0170        0    C0402               
C12                  10.8090       39.7940      180    C0402               
C24                  22.4130       46.1060        0    C0402               
C25                  22.4130       45.1060        0    C0402               
C27                  28.3350       40.9370      180    C0402               
C59                  49.9420       82.8030      270    C0402               
C71                  22.9340      124.8810      180    C0402               
C107                 30.4910      102.8610      180  m C0402               
C110                 30.4910       98.7970      180  m C0402               
C51                  53.8350       70.6630      270    C0805               
C52                  52.9420       81.2530      270    C0805               
C53                  54.9420       81.2530      270    C0805               
C54                  59.9420       81.2530      270    C0805               
C55                  61.9420       81.2530      270    C0805               
C65                  23.8840      126.3810      180    C0805               
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
LD7                  94.7886       24.8588       90    D1206               
LD6                  25.4320       79.4480      270    D1206               
LD4                  16.4320       79.4480      270    D1206               
LD3                  19.4320       79.4480      270    D1206               
RN1                  17.6150       59.6450      270    ARC241_SO8          
RN2                  4.1150        59.6450      270    ARC241_SO8          
RZ1                  17.9400       71.1940        0    ARC241_SO8          
RZ2                  29.7020       79.2180        0    ARC241_SO8          
R63                  55.1920       94.8530        0    C0603               
R61                  54.9560      115.3070        0    C0603               
R48                  33.3410      131.5970      270    C0603               
R67                  -3.3610      152.8990        0  m C0603               
R7                   66.6240      115.7630      180    C0603               
R56                  45.9420       88.6030      270    C0603               
R57                  38.8150       62.5900       90  m C0603               
R58                  47.4510       62.5900       90  m C0603               
R59                  44.4420       88.6030      270    C0603               
R60                  55.1920       93.3530        0    C0603               
R62                  55.1860       96.3090        0    C0603               
SW3                  29.2970       68.4020       90    SW_TYCO_1571983-4   
SW1                  42.8470       61.8110       90    OMRON_B3SN-3012     
SW2                  51.4830       61.8110       90    OMRON_B3SN-3012     
SW4                  64.5670       98.9180       90    OMRON_B3SN-3012     
R53                  23.8170      100.1940      180    C0603               
IC15                 38.3170       68.0350       90    SON50P300X200X100-9N-R175X155
J10                  14.2390       54.7550       90    SAMTEC_TSM-106-01-X-DV
LD2                  22.4320       79.4480      270    D1206               
LD5                  13.4320       79.4480      270    D1206               
LD1                  58.4020      120.8370      270    D1206               
R70                  25.4320       72.6980       90    C0603               
R52                  60.9130      121.0100      270    C0603               
R50                  17.0050       87.6820      270    C0603               
C34                  79.7398        0.5764        0  m C0603               
C88                  80.2906       46.2504        0  m C0603               
J1                   70.7450      198.9860      270  m CON150_QTSDA        
R44                  70.7602       46.7924       90  m C0603               
R51                  20.2550       87.9320      180    C0603               
R46                  66.1200      111.7390      270    C0603               
R47                  64.7110      110.2270      180    C0603               
U2                   20.7496       83.9922      180    SOT23-5             
R32                  29.0570       84.7100        0  m C0603               
R34                  27.8070       86.4600      270  m C0603               
R26                  35.9380       84.7100        0  m C0603               
R28                  34.4380       83.2100        0  m C0603               
R30                  32.0570       84.7100        0  m C0603               
R33                  29.3070       86.4600      270  m C0603               
R35                  25.8070       87.9600      270  m C0603               
R3                   37.4060       83.1760        0  m C0603               
R25                  35.6880       86.4600      270  m C0603               
R27                  34.1880       86.4600      270  m C0603               
R29                  32.6880       86.4600      270  m C0603               
R31                  30.8070       86.4600      270  m C0603               
QZ1                  36.8760       74.3480        0    OSC_SILABS_SI570    
IC1                  58.8330       71.6190        0    SOP65P490X95-8N     
IC9                  58.8330       76.6190        0    SOP65P490X95-8N     
J8                   23.9480      142.0290      270    CON14MD_2MM         
L5                   56.6920       81.3530        0    C0603               
L6                   61.9420       83.1030       90    C0603               
L7                   48.4420       81.6030       90    C0603               
L8                   25.4960      123.2380        0    C0603               
Z1                   55.4460       70.7028        0    SOT23               
QZ2                  45.8720       72.3270        0    OSCSC254P490X696X180-6N
U1                   46.1480       75.9940       90    OSC_4PIN_53S        
R54                  55.3110      110.8530      180    C0603               
R55                  51.7690      118.3430      270    C0603               
R20                  20.2650      120.0700       90    C0603               
R21                  14.4230      120.0700       90    C0603               
R14                  55.3450       72.3060      180    C0603               
R15                  51.4000       74.2860        0    C0603               
R16                  55.1150       74.5920        0    C0603               
R17                  50.6540       67.2260        0  m C0603               
IC11                 14.6110      127.9800        0    QFN50P500X500X100-33N-S355
LC1                  56.0306       -1.2950      180    MURATA_BNX02        
LC3                  57.7324       44.1202      180    MURATA_BNX02        
LC2                  57.5800       23.3430      180    MURATA_BNX02        
C44                  9.2820       102.6070        0    C0402               
C103                 73.9390      122.9560      180    C0603               
C100                 36.4320       70.7850      270    C0603               
C31                  35.6400       87.9900      270    C0603               
C48_1                54.1550      153.2895      270  m C0603               
C52_1                61.5256      146.4027      270  m C0603               
C53_1                19.4830      150.3896      180  m C0603               
C54_1                50.1699      151.2392      180  m C0603               
C48                  20.5270       97.7930       90    C0603               
C41                  41.3470        1.5550      270    C0603               
C95                  43.0488       46.9448      270    C0603               
C84                  41.2896       23.3510        0    C0603               
C42                  14.1570      104.4370      180    C0603               
C46                  17.9870       97.7930       90    C0603               
C13                  11.1090       42.0800      180    C0603               
C23                  6.0530        42.0800        0    C0603               
C28                  28.6350       42.2070      180    C0603               
C30                  23.5790       42.2070        0    C0603               
C47                  19.2570       97.7930       90    C0603               
C33                  81.8518        6.9660      180    CAPC3225X279N       
C35                  81.8360       10.4316      180    CAPC3225X279N       
C36                  81.8574        3.4302      180    CAPC3225X279N       
C37                  81.8614       -0.0586      180    CAPC3225X279N       
C87                  82.4056       52.6154      180    CAPC3225X279N       
C89                  82.4056       56.1154      180    CAPC3225X279N       
C90                  82.4056       45.6154      180    CAPC3225X279N       
C91                  82.4056       49.1154      180    CAPC3225X279N       
C76                  82.2424       33.1900      180    CAPC3225X279N       
C78                  82.2678       29.6848      180    CAPC3225X279N       
C79                  82.2678       26.1796      180    CAPC3225X279N       
C80                  82.2678       22.6744      180    CAPC3225X279N       
C38                  70.7348       16.4274      270    C1210               
C39                  66.7470       16.4274      270    C1210               
C92                  67.2630       62.0700      270    C1210               
C93                  71.3270       62.0700      270    C1210               
C81                  71.1412       39.1858      270    C1210               
C82                  67.1280       39.1604      270    C1210               
J6                   3.7300        26.8000       90    TYCO_1367073        
J7                   22.7300       26.8000       90    TYCO_1367073        
IC13                 68.0580      117.5590      180    SOP65P490X110-8N    
C32                  75.3576       14.9528        0    C7343POL            
C86                  75.9056       60.6154        0    C7343POL            
C75                  75.7386       37.6858        0    C7343POL            
C40                  63.1816       14.7726      180    POSCAP_D3           
C94                  63.4530       60.4430      180    POSCAP_D3           
C83                  63.4102       37.5056      180    POSCAP_D3           
C85                  10.6210       94.0980        0    POSCAP_D3           
L9                   23.3420      104.3530      180    INDC2012X90N        
L1                   9.7240        45.7740      270    INDC2012X90N        
L2                   7.4380        43.9740       90    INDC2012X90N        
L3                   27.2500       45.9010      270    INDC2012X90N        
L4                   24.9640       44.1010       90    INDC2012X90N        
RG1                  11.9912      101.7674        0    QFN50P400X500X80-29N-R375X275
IC10                 68.9314        3.6244      270    LGA133S127P12X12_05-08-1766
IC14                 69.4902       49.2936      270    LGA133S127P12X12_05-08-1766
IC4                  69.3378       26.3574      270    LGA133S127P12X12_05-08-1766
R13                  10.1820      101.5910      180    C0402               
R72                  66.8940       20.0570      180  m C0603               
R73                  67.0210       43.0440      180  m C0603               
R74                  66.3860       -2.6760      180  m C0603               
R10                  75.8910        2.3932       90  m C0603               
R43                  76.4498       48.0624       90  m C0603               
R38                  76.2974       25.1262       90  m C0603               
R12                  80.5526       -2.8272      180    C0603               
R45                  81.1114       42.8420      180    C0603               
R40                  80.9590       19.9058      180    C0603               
R18                  20.5190      132.1110      270    C0603               
R19                  17.4710      120.0700       90    C0603               
R22                  19.1220      132.1110      270    C0603               
R23                  18.8680      120.0700       90    C0603               
R24                  15.8200      120.0700       90    C0603               
R8                   76.7760       -1.4060        0  m C0603               
R9                   75.2760       -2.8030      180  m C0603               
R41                  77.2840       44.4410        0  m C0603               
R42                  75.7840       42.9170      180  m C0603               
R36                  77.1744       21.5060        0  m C0603               
R37                  75.6744       20.0328      180  m C0603               
R39                  70.6078       23.8562       90  m C0603               
LK1                  60.1684       21.3028        0    1-HOLE_0-8P         
LK2                  60.2954       44.2390        0    1-HOLE_0-8P         
LK3                  65.8660      107.6870        0    1-HOLE_0-8P         
LK4                  19.5110      104.3850        0    1-HOLE_0-8P         
LK5                  63.7070      102.9880        0    1-HOLE_0-8P         
LK6                  43.1330      130.4200        0    1-HOLE_0-8P         
LK7                  36.2750       11.2940        0    1-HOLE_0-8P         
LK8                  -1.5790      147.7440        0    1-HOLE_0-8P         
LK9                  -5.3890      147.8710        0    1-HOLE_0-8P         
LK1_1                79.5470      148.2455        0    1-HOLE_0-8P         
LK2_1                16.0470      149.7695        0    1-HOLE_0-8P         
LK3_1                10.4590      173.1375        0    1-HOLE_0-8P         
LK4_1                79.5470      170.5975        0    1-HOLE_0-8P         
LK5_1                79.5470      166.5335        0    1-HOLE_0-8P         
LK6_1                75.4830      169.5815        0    1-HOLE_0-8P         
LK7_1                75.4830      165.5175        0    1-HOLE_0-8P         
LK8_1                10.4590      175.1695        0    1-HOLE_0-8P         
LK9_1                79.5470      164.5015        0    1-HOLE_0-8P         
LK10_1               75.4830      161.4535        0    1-HOLE_0-8P         
LK11_1               10.4590      162.9775        0    1-HOLE_0-8P         
LK12_1               16.0470      155.8655        0    1-HOLE_0-8P         
LK13_1               79.5470      156.3735        0    1-HOLE_0-8P         
LK14_1               10.4590      152.8175        0    1-HOLE_0-8P         
LK15_1               16.0470      147.7375        0    1-HOLE_0-8P         
LK16_1               16.0470      178.2175        0    1-HOLE_0-8P         
LK17_1               10.4590      154.8495        0    1-HOLE_0-8P         
LK18_1               16.0470      176.1855        0    1-HOLE_0-8P         
LK19_1               16.0470      157.8975        0    1-HOLE_0-8P         
LK20_1               16.0470      163.9935        0    1-HOLE_0-8P         
LK21_1               75.4830      159.4215        0    1-HOLE_0-8P         
LK22_1               10.4590      167.0415        0    1-HOLE_0-8P         
LK23_1               79.5470      154.3415        0    1-HOLE_0-8P         
LK24_1               10.4590      158.9135        0    1-HOLE_0-8P         
LK25_1               16.0470      161.9615        0    1-HOLE_0-8P         
LK26_1               79.5470      146.2135        0    1-HOLE_0-8P         
LK27_1               10.4590      156.8815        0    1-HOLE_0-8P         
LK28_1               79.5470      152.3095        0    1-HOLE_0-8P         
LK29_1               75.4830      151.2935        0    1-HOLE_0-8P         
LK30_1               7.6650       156.8815        0    1-HOLE_0-8P         
LK31_1               10.4590      179.4875        0    1-HOLE_0-8P         
LK32_1               16.0470      166.0255        0    1-HOLE_0-8P         
LK33_1               16.0470      151.8015        0    1-HOLE_0-8P         
LK34_1               79.5470      160.4375        0    1-HOLE_0-8P         
LK35_1               16.0470      182.5355        0    1-HOLE_0-8P         
LK36_1               10.4590      160.9455        0    1-HOLE_0-8P         
LK37_1               10.4590      146.7215        0    1-HOLE_0-8P         
LK38_1               79.5470      162.4695        0    1-HOLE_0-8P         
LK39_1               10.4590      181.5195        0    1-HOLE_0-8P         
LK40_1               75.4830      155.3575        0    1-HOLE_0-8P         
LK41_1               79.5470      168.5655        0    1-HOLE_0-8P         
LK42_1               10.4590      177.2015        0    1-HOLE_0-8P         
LK43_1               16.0470      168.0575        0    1-HOLE_0-8P         
LK44_1               10.4590      150.7855        0    1-HOLE_0-8P         
LK45_1               79.5470      158.4055        0    1-HOLE_0-8P         
LK46_1               75.4830      167.5495        0    1-HOLE_0-8P         
LK47_1               16.0470      145.7055        0    1-HOLE_0-8P         
LK48_1               16.0470      153.8335        0    1-HOLE_0-8P         
LK49_1               75.4830      157.3895        0    1-HOLE_0-8P         
LK50_1               16.0470      159.9295        0    1-HOLE_0-8P         
LK51_1               75.4830      149.2615        0    1-HOLE_0-8P         
LK52_1               79.5470      150.2775        0    1-HOLE_0-8P         
LK53_1               16.0470      170.0895        0    1-HOLE_0-8P         
LK54_1               32.8110      140.6255        0    1-HOLE_0-8P         
LK55_1               34.8430      138.4665        0    1-HOLE_0-8P         
LK56_1               36.8750      140.6255        0    1-HOLE_0-8P         
LK57_1               16.0470      180.5035        0    1-HOLE_0-8P         
LK58_1               75.4830      163.4855        0    1-HOLE_0-8P         
LK59_1               10.4590      148.7535        0    1-HOLE_0-8P         
LK60_1               16.0470      184.5675        0    1-HOLE_0-8P         
LK61_1               16.0470      174.1535        0    1-HOLE_0-8P         
LK62_1               10.4590      171.1055        0    1-HOLE_0-8P         
LK63_1               75.4830      153.3255        0    1-HOLE_0-8P         
LK64_1               16.0470      172.1215        0    1-HOLE_0-8P         
LK65_1               10.4590      169.0735        0    1-HOLE_0-8P         
LK66_1               10.4590      183.5515        0    1-HOLE_0-8P         
LK67_1               10.4590      165.0095        0    1-HOLE_0-8P         
LK68_1               75.4830      147.2295        0    1-HOLE_0-8P         
C49                  12.3330      128.8210      180    C0402               
C1                   64.1650      117.5410        0  m C0402               
C2                   76.8920       70.3530        0  m C0402               
C4                   73.5470      126.2810        0  m C0402               
C5                   80.9920       82.8530      180  m C0402               
C6                   67.3920       72.8530        0  m C0402               
C7                   71.3850       83.9380      180  m C0402               
C8                   66.8920       78.8530        0  m C0402               
C14                  34.9420       77.9030       90    C0402               
C15                  12.3150      124.8570      180    C0402               
C16                  8.2660        88.8910        0    C0402               
C17                  8.3930       104.1310        0    C0402               
C18                  8.2660        87.8750        0    C0402               
C19                  12.3330      127.8050      180    C0402               
C20                  8.3010       105.1620        0    C0402               
C21                  12.3330      125.7730      180    C0402               
C45                  9.2820       100.5750        0    C0402               
C60                  49.2000       75.9890      180  m C0402               
C61                  16.8360      120.7510      270  m C0402               
C77                  79.8462       23.3094        0  m C0402               
C128                 17.4420       65.9030       90    C0402               
C130                 47.4510       87.4250      270  m C0402               
C131                 11.5760       45.1730       90    C0402               
C132                 28.9420       45.3000       90    C0402               
C134                 32.4420      106.9030      270  m C0402               
C137                 42.4920      102.8530      180  m C0402               
C140                 40.4500      107.7560       90  m C0402               
C141                 39.8310       88.3140      270  m C0402               
C143                 44.3450      113.7830        0  m C0402               
C144                 31.9570      116.0110       90  m C0402               
C146                 50.4610       92.9880      270  m C0402               
C147                 34.7510      116.0110       90  m C0402               
C149                 23.3790      102.0990      180  m C0402               
C150                 22.3630       89.6530        0    C0402               
C152                 50.3630      102.8690        0  m C0402               
C154                 32.4920      102.8530      180  m C0402               
C156                 37.6030      113.7830      180  m C0402               
C158                 26.1150       95.8180       90  m C0402               
C159                 55.0200      109.3680      180    C0402               
C160                 40.4660      108.8880      270  m C0402               
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
J3_1                 69.3870      152.0555      270    CONHE13D3X1M        
J4_1                 69.3870      177.7095      270    CONHE13D3X1M        
J1_1                 76.9850      176.4995      270    SAMTEC_SSW-103-01-G-D
J2                   95.3650      139.7200        0    HARTING_0903196X921 
J3                   -9.1150       50.8200      180    HARTING_09732966801 
D1_1                 52.8550      148.7395        0  m SOD323_INV          
U1_1                 59.4950      178.9795      270    PQFP240_050         
R20_1                33.0450      157.6995      180  m C0402               
R21_1                35.9450      157.6995        0  m C0402               
R22_1                33.0450      159.6995      180  m C0402               
R23_1                35.9450      159.6995        0  m C0402               
R25_1                31.0324      165.1165      180  m C0402               
R26_1                23.5450      165.1995      180  m C0402               
R28_1                33.9450      162.6995        0  m C0402               
R29_1                35.9450      162.6995        0  m C0402               
R30_1                24.4450      161.1995        0  m C0402               
R31_1                23.5450      162.1995      180  m C0402               
R32_1                31.0476      153.2569      180  m C0402               
R33_1                31.9476      152.0109        0  m C0402               
R34_1                54.4450      171.6995        0  m C0402               
R35_1                53.5450      170.6995      180  m C0402               
R36_1                31.0246      147.7191      180  m C0402               
R37_1                23.5443      148.1433      180  m C0402               
R14_1                35.0625      161.6673      180  m C0402               
R17_1                55.9450      158.6995        0  m C0402               
R78                  14.3100      130.7930        0    C0402               
R1                   81.9420       68.8030       90  m C0402               
R2                   81.9420       75.3030       90  m C0402               
R6                   72.5970       79.9430       90  m C0402               
R24_1                63.7990      150.7275      270    C0402               
R3_1                 58.7835      147.9388        0  m C0402               
R4_1                 23.5443      150.5662      180  m C0402               
R5_1                 31.0476      163.9055      180  m C0402               
R6_1                 56.8478      174.7564        0  m C0402               
R7_1                 55.9450      169.1995        0  m C0402               
R8_1                 31.0450      173.6995      180  m C0402               
R9_1                 55.9353      167.8937        0  m C0402               
R10_1                32.9763      167.1576      180  m C0402               
R11_1                55.9864      166.0878        0  m C0402               
R12_1                24.4450      157.1995        0  m C0402               
R13_1                55.9450      161.6995        0  m C0402               
R15_1                24.4450      154.6995        0  m C0402               
R16_1                24.4450      152.6995        0  m C0402               
R27_1                34.0050      151.3895      180  m C0402               
R46_1                62.9743      146.7405      270  m C0402               
R47_1                19.7509      149.0089      180  m C0402               
R4                   72.2850       82.6680        0  m C0402               
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

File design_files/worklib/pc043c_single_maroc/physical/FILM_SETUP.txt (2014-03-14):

(axlfcreate "PASTEMASK_BOTTOM" '(0 0 0 0 25400 1 0 0 0 0 0 1 1)
	'("PIN/PASTEMASK_BOTTOM" "PACKAGE GEOMETRY/PASTEMASK_BOTTOM" ))
(axlfcreate "ASSEMBLY_BOTTOM" '(0 0 0 2000 25400 1 0 0 0 0 0 1 1)
	'("REF DES/ASSEMBLY_BOTTOM" "PACKAGE GEOMETRY/ASSEMBLY_BOTTOM" "DRAWING FORMAT/OUTLINE" "DRAWING FORMAT/TITLE_BLOCK" "DRAWING FORMAT/TITLE_DATA" "DRAWING FORMAT/REVISION_BLOCK" "DRAWING FORMAT/REVISION_DATA" "BOARD GEOMETRY/OUTLINE" "BOARD GEOMETRY/DIMENSION" ))
(axlfcreate "SOLDERMASK_TOP" '(0 0 0 0 25400 1 0 0 0 0 0 1 1)
	'("PIN/SOLDERMASK_TOP" "PACKAGE GEOMETRY/SOLDERMASK_TOP" "BOARD GEOMETRY/SOLDERMASK_TOP" ))
(axlfcreate "SOLDERMASK_BOTTOM" '(0 0 0 0 25400 1 0 0 0 0 0 1 1)
	'("PIN/SOLDERMASK_BOTTOM" "PACKAGE GEOMETRY/SOLDERMASK_BOTTOM" "BOARD GEOMETRY/SOLDERMASK_BOTTOM" ))
(axlfcreate "SILKSCREEN_TOP" '(0 0 0 2500 25400 1 0 0 0 0 0 1 1)
	'("REF DES/SILKSCREEN_TOP" "BOARD GEOMETRY/SILKSCREEN_TOP" ))
(axlfcreate "SILKSCREEN_BOTTOM" '(0 0 0 2500 25400 1 0 0 0 0 0 1 1)
	'("REF DES/SILKSCREEN_BOTTOM" "BOARD GEOMETRY/SILKSCREEN_BOTTOM" ))
(axlfcreate "DRILL_FIGURE" '(0 0 0 5000 25400 1 0 0 0 0 0 1 0)
	'("MANUFACTURING/NCDRILL_LEGEND" "MANUFACTURING/NCDRILL_FIGURE" "MANUFACTURING/NCLEGEND-1-6" "DRAWING FORMAT/OUTLINE" "DRAWING FORMAT/TITLE_BLOCK" "DRAWING FORMAT/TITLE_DATA" "DRAWING FORMAT/REVISION_BLOCK" "DRAWING FORMAT/REVISION_DATA" "BOARD GEOMETRY/OUTLINE" ))
(axlfcreate "OUTLINE" '(0 0 0 1000 25400 1 0 0 0 0 0 1 1)
	'("BOARD GEOMETRY/OUTLINE" ))
(axlfcreate "PASTEMASK_TOP" '(0 0 0 0 25400 1 0 0 0 0 0 1 1)
	'("PIN/PASTEMASK_TOP" "PACKAGE GEOMETRY/PASTEMASK_TOP" ))
(axlfcreate "ASSEMBLY_TOP" '(0 0 0 2000 25400 1 0 0 0 0 0 1 1)
	'("REF DES/ASSEMBLY_TOP" "PACKAGE GEOMETRY/ASSEMBLY_TOP" "DRAWING FORMAT/OUTLINE" "DRAWING FORMAT/TITLE_BLOCK" "DRAWING FORMAT/TITLE_DATA" "DRAWING FORMAT/REVISION_BLOCK" "DRAWING FORMAT/REVISION_DATA" "BOARD GEOMETRY/OUTLINE" "BOARD GEOMETRY/DIMENSION" ))
(axlfcreate "BOTTOM" '(0 0 0 0 25400 1 0 0 0 0 0 1 1)
	'("ETCH/BOTTOM" "PIN/BOTTOM" "VIA CLASS/BOTTOM" ))
(axlfcreate "L5" '(0 0 0 0 25400 1 0 0 0 0 0 1 1)
	'("ETCH/L5" "PIN/L5" "VIA CLASS/L5" ))
(axlfcreate "L4" '(0 0 0 0 25400 1 0 0 0 0 0 1 1)
	'("ETCH/L4" "PIN/L4" "VIA CLASS/L4" ))
(axlfcreate "L3" '(0 0 0 0 25400 1 0 0 0 0 0 1 1)
	'("ETCH/L3" "PIN/L3" "VIA CLASS/L3" ))
(axlfcreate "L2" '(0 0 0 0 25400 1 0 0 0 0 0 1 1)
	'("ETCH/L2" "PIN/L2" "VIA CLASS/L2" ))
(axlfcreate "TOP" '(0 0 0 0 25400 1 0 0 0 0 0 1 1)
	'("ETCH/TOP" "PIN/TOP" "VIA CLASS/TOP" ))

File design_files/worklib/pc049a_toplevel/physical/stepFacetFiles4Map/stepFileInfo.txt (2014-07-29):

#STEP_FILE ! FILE_SIZE | MOD_TIME

QTS-075-01-X-D-A-GP.step ! 5915904 ! 1380700706
c-1489779-01-c-3d.stp ! 1160451 ! 1188653396
c-1489779-01-c-3d_2_rotated.stp ! 2006475 ! 1399908411
13137.stp ! 337741 ! 1282212988
Samtec-HDMI-19-01-S-SM-PF.step ! 978091 ! 1399555822
c-1489779-01-c-3d_1_rotated.stp ! 2006594 ! 1399906186
0973_DIN_har-bus_R_angled_female_96_pole.stp ! 342697 ! 1210334864
0903_DIN_Type_C_angled_male_96_pole.stp ! 220246 ! 1091451840

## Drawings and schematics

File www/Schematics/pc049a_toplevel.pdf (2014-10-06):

# MAROC

## FPGA CONNECTIONS

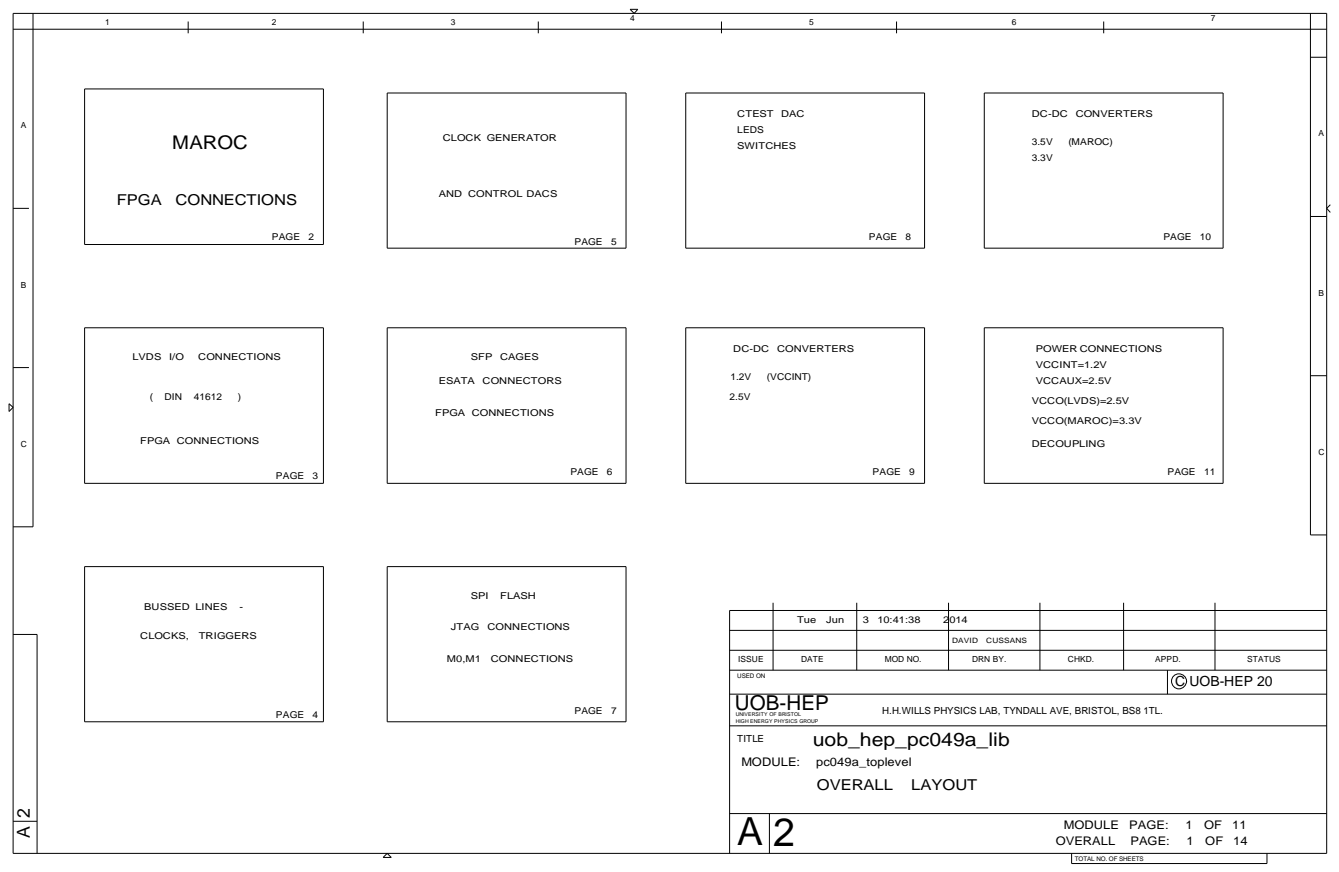
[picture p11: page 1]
(VCCINT); PAGE 9; VCCO(MAROC)=3.3V; VCCO(LVDS)=2.5V; VCCAUX=2.5V; VCCINT=1.2V; DECOUPLING; POWER CONNECTIONS; PAGE 11; CTEST DAC LEDS SWITCHES; PAGE 8 PAGE 5; CLOCK GENERATOR; SFP CAGES; FPGA CONNECTIONS; ESATA CONNECTORS; PAGE 6; PAGE 2; (MAROC); JTAG CONNECTIONS; M0,M1 CONNECTIONS; SPI FLASH; PAGE 7; LVDS I/O; CONNECTIONS; ( DIN 41612; BUSSED LINES -; CLOCKS, TRIGGERS; PAGE 4; PAGE 3; OVERALL LAYOUT; PAGE 10; OVERALL PAGE:; MODULE PAGE:; uob_hep_pc049a_lib; UOB-HEP

DC-DC CONVERTERS

AND CONTROL DACS

Tue Jun | 3 10:41:38 2014

DAVID CUSSANS

ISSUE | DATE | MOD NO. | DRN BY. | CHKD. | APPD. | STATUS

USED ON | C UOB-HEP 20

UNIVERSITY OF BRISTOL
HIGH ENERGY PHYSICS GROUP
TITLE
MODULE: pc049a_toplevel

H.H.WILLS PHYSICS LAB, TYNDALL AVE, BRISTOL, BS8 1TL.

TOTAL NO. OF SHEETS

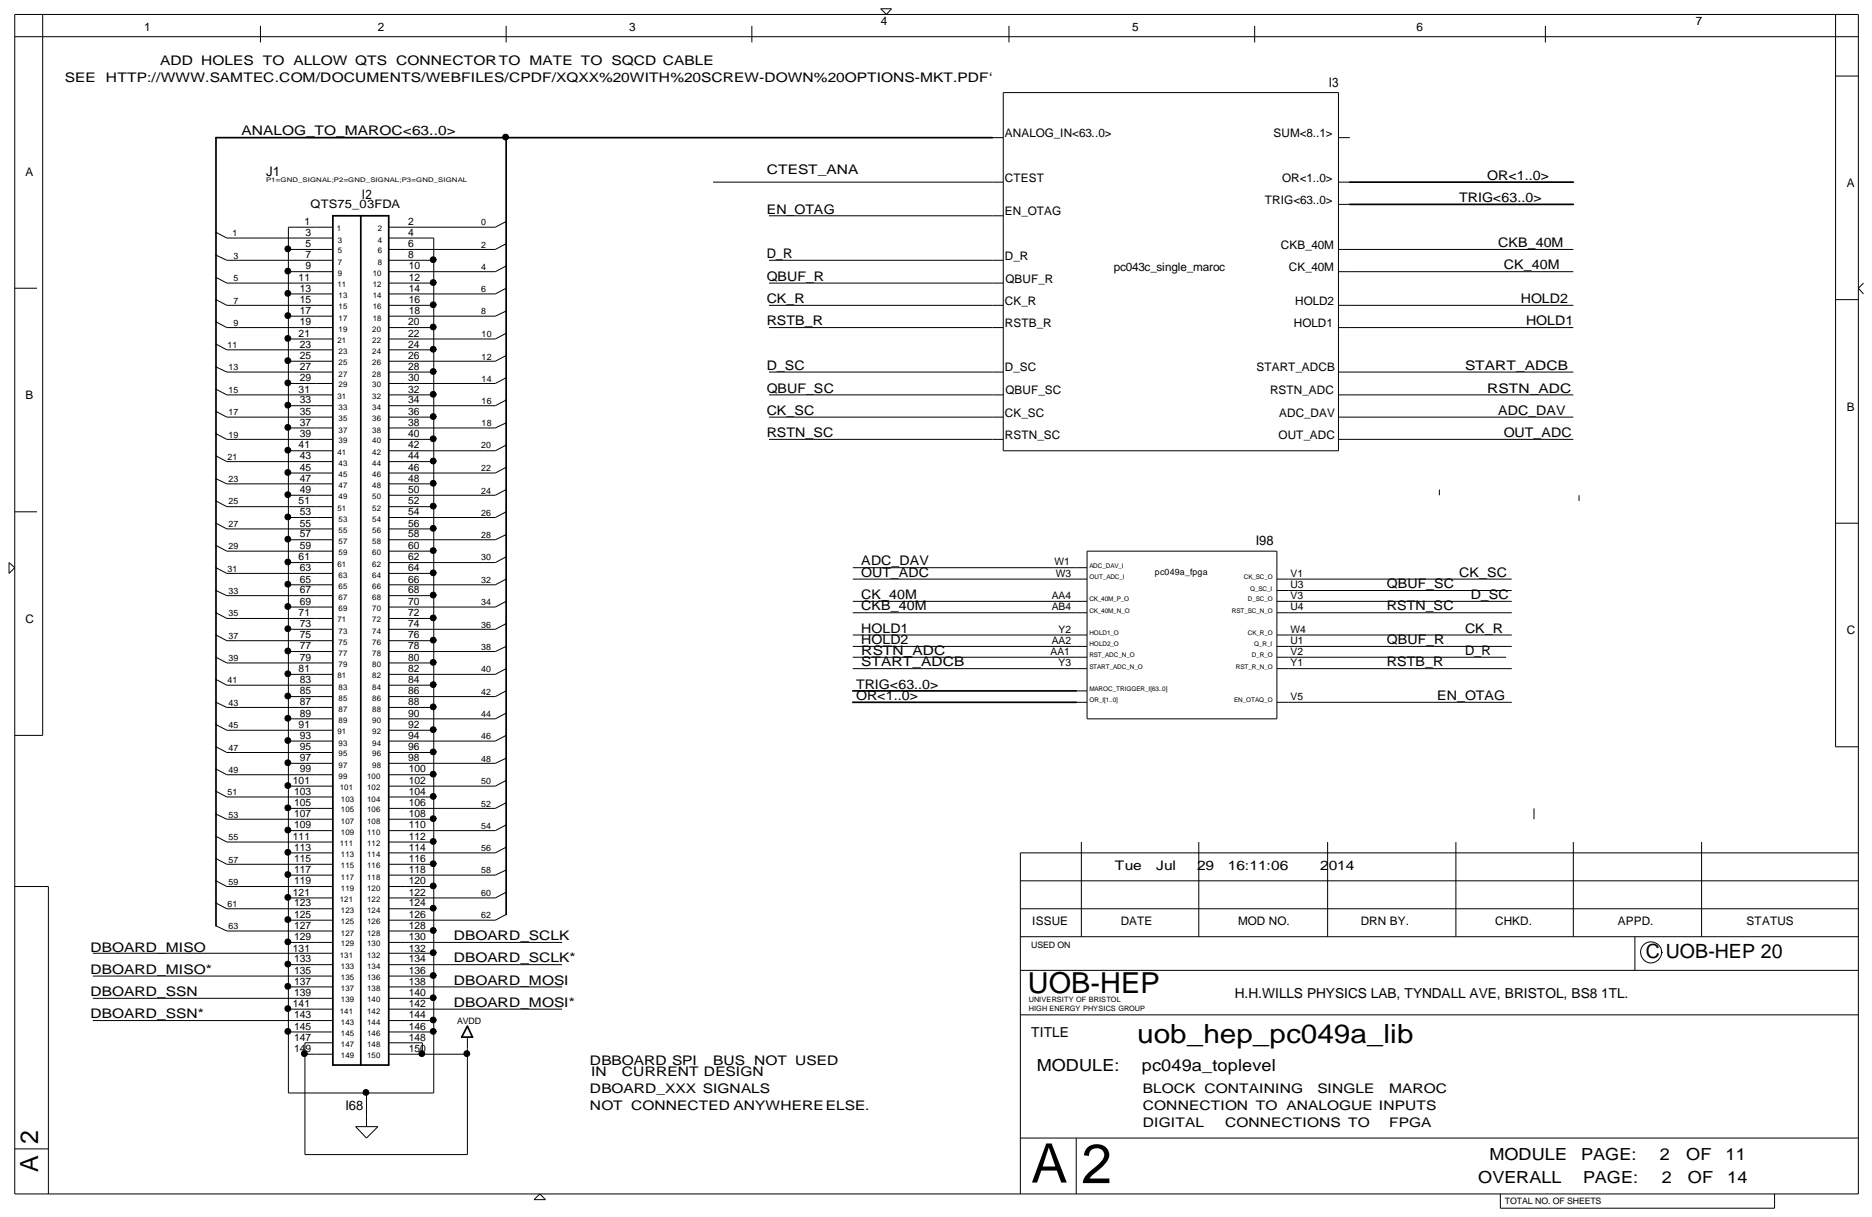
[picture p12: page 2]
DIGITAL; CONNECTIONS TO; FPGA; Tue Jul; OVERALL PAGE:; MODULE PAGE:; uob_hep_pc049a_lib; ANALOG_TO_MAROC<63..0>; DBOARD_MOSI; DBOARD_SCLK*; DBOARD_MOSI*; P1=GND_SIGNAL;P2=GND_SIGNAL;P3=GND_SIGNAL; CTEST_ANA; QBUF_SC; RSTB_R; QBUF_SC RSTN_SC; QBUF_R RSTB_R; EN_OTAG; ADC_DAV OUT_ADC CK_40M CKB_40M HOLD1 HOLD2 RSTN_ADC; TRIG<63..0>; START_ADCB; OR<1..0> TRIG<63..0>; CK_SC RSTN_SC; QBUF_R; START_ADCB RSTN_ADC; HOLD2 HOLD1; CKB_40M; OUT_ADC; ADC_DAV; DBOARD_SCLK; QTS75_03FDA; DBOARD_SSN*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

ADD HOLES TO ALLOW QTS CONNECTORTO MATE TO SQCD CABLE

SEE HTTP://WWW.SAMTEC.COM/DOCUMENTS/WEBFILES/CPDF/XQXX%20WITH%20SCREW-DOWN%20OPTIONS-MKT.PDF‘

UNIVERSITY OF BRISTOL
HIGH ENERGY PHYSICS GROUP
TITLE
MODULE: pc049a_toplevel

H.H.WILLS PHYSICS LAB, TYNDALL AVE, BRISTOL, BS8 1TL.

DBBOARD SPI BUS NOT USED
IN CURRENT DESIGN
DBOARD_XXX SIGNALS
NOT CONNECTED ANYWHERE ELSE.

BLOCK CONTAINING SINGLE MAROC
CONNECTION TO ANALOGUE INPUTS

TOTAL NO. OF SHEETS

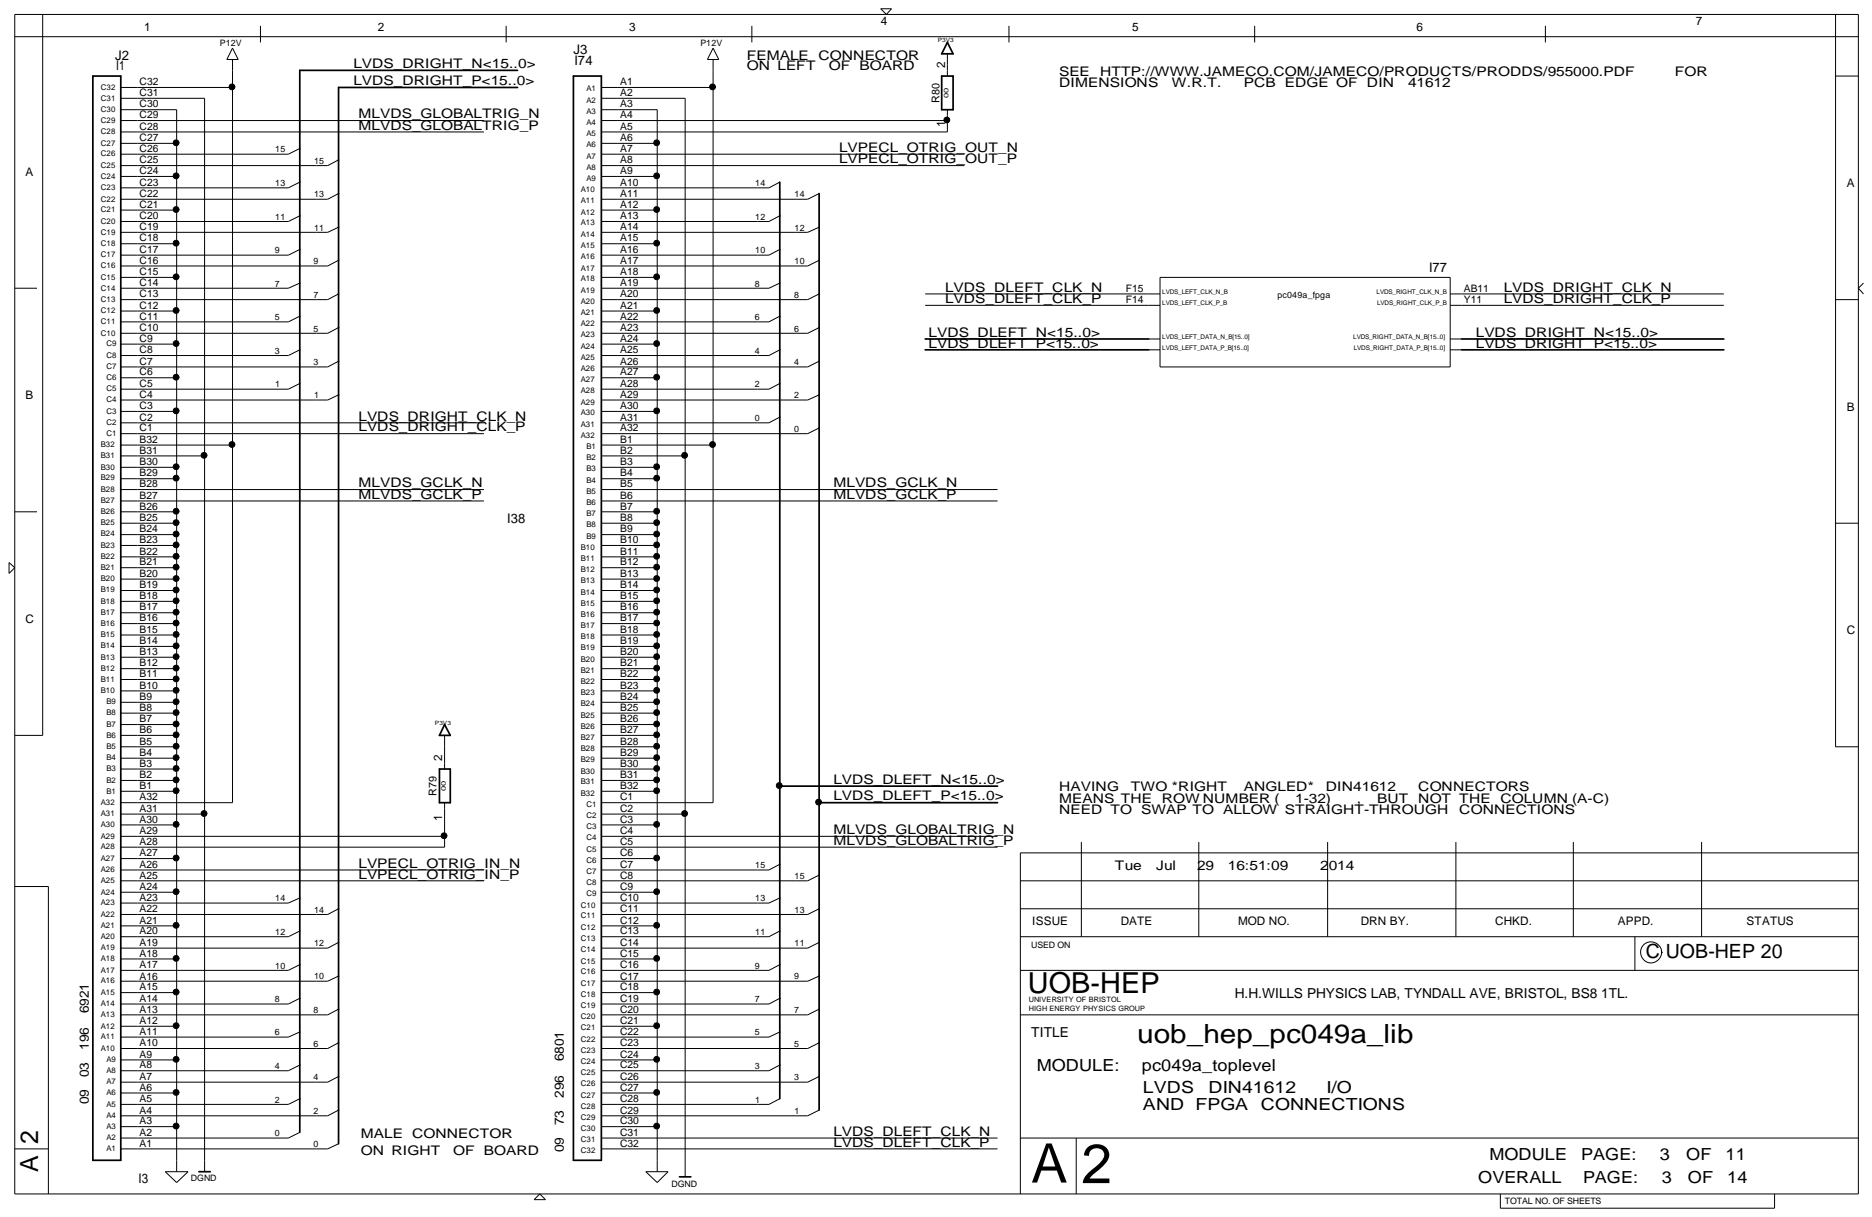
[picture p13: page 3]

FEMALE CONNECTOR
ON LEFT OF BOARD

A5
A6

A28
A27

ISSUE | DATE | MOD NO. | DRN BY. | CHKD. | APPD. | STATUS

USED ON | C UOB-HEP 20

H.H.WILLS PHYSICS LAB, TYNDALL AVE, BRISTOL, BS8 1TL.

MALE CONNECTOR
ON RIGHT OF BOARD

TOTAL NO. OF SHEETS

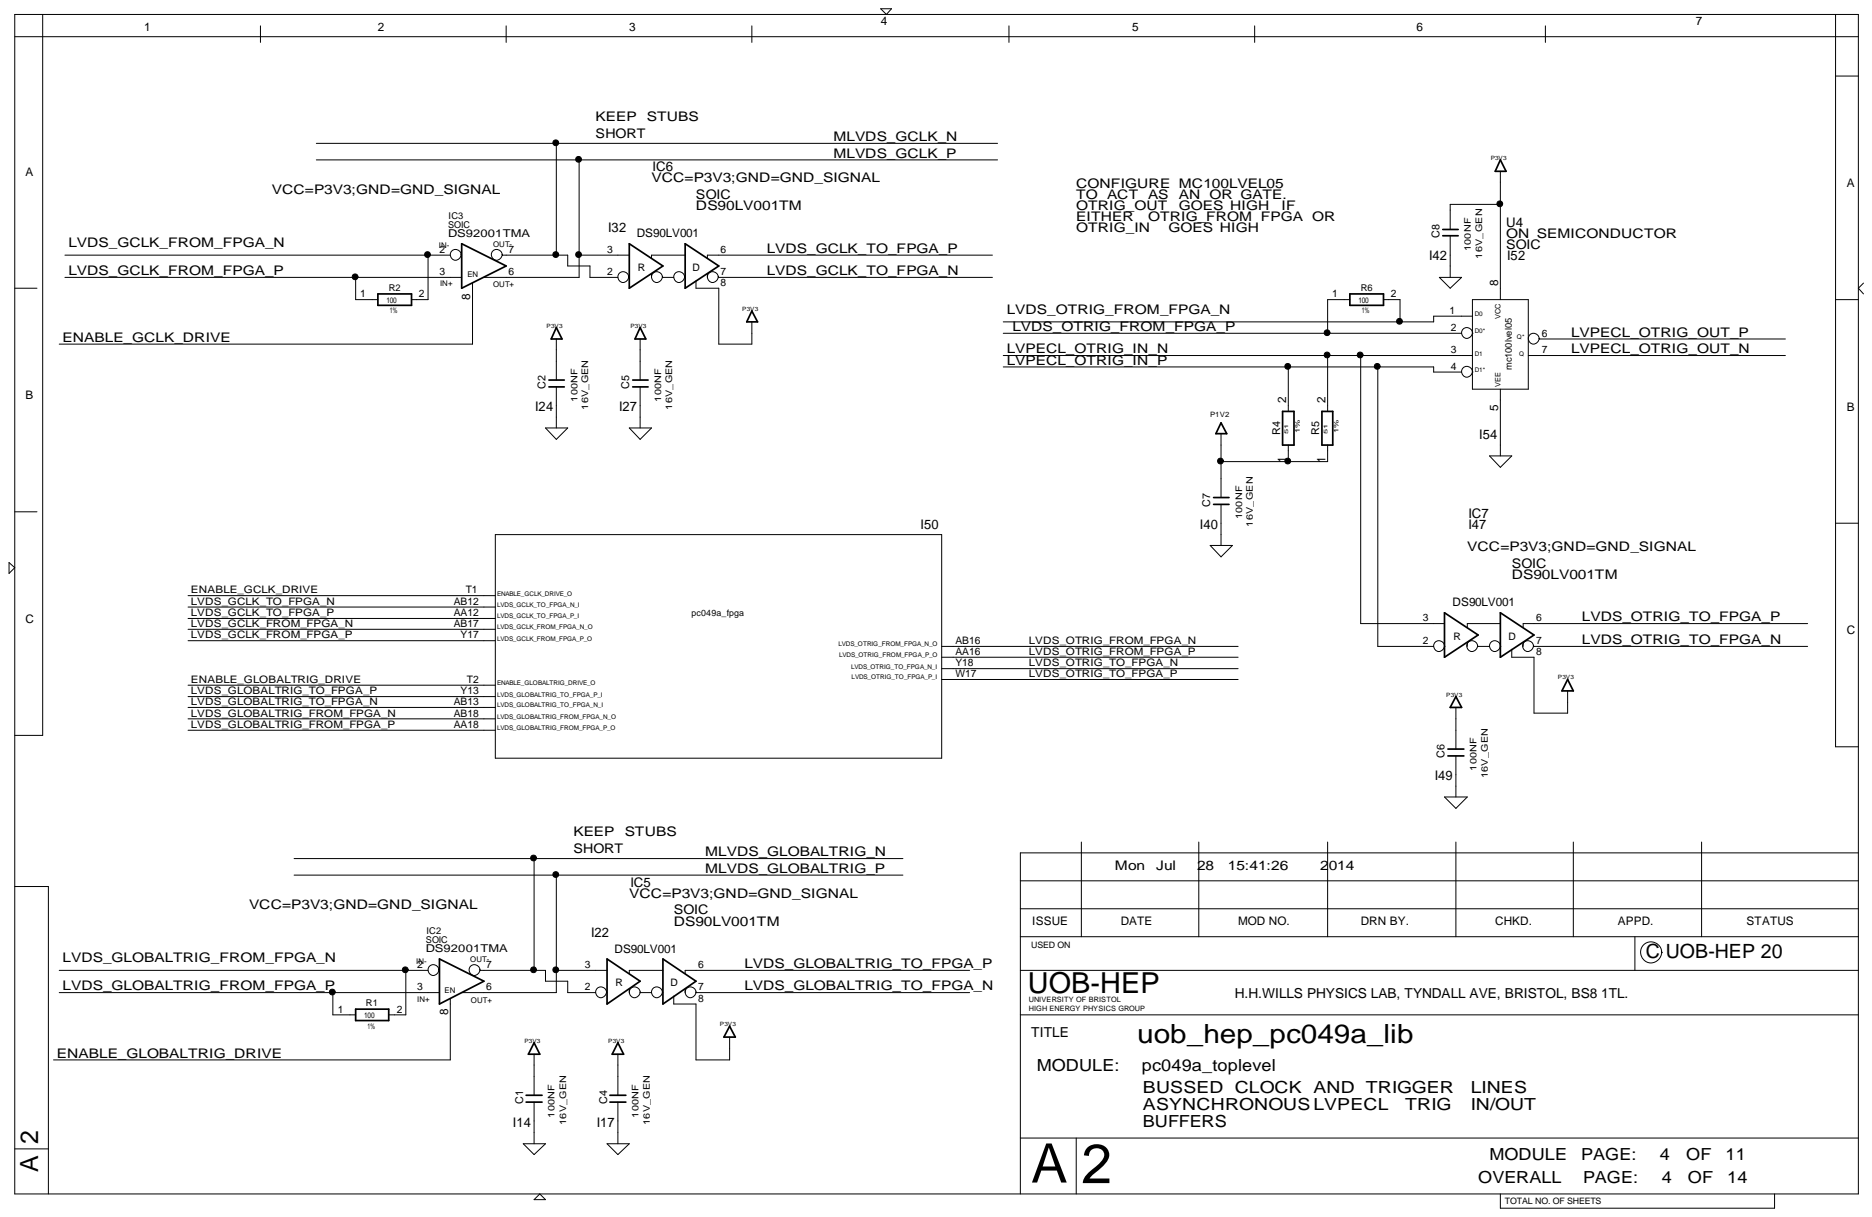
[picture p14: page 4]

CONFIGURE MC100LVEL05
TO ACT AS AN OR GATE.
OTRIG_OUT GOES HIGH IF
OTRIG_IN GOES HIGH EITHER OTRIG_FROM FPGA OR

ISSUE | DATE | MOD NO. | DRN BY. | CHKD. | APPD. | STATUS

USED ON | C UOB-HEP 20

H.H.WILLS PHYSICS LAB, TYNDALL AVE, BRISTOL, BS8 1TL.

BUSSED CLOCK AND TRIGGER LINES
ASYNCHRONOUS LVPECL TRIG IN/OUT
BUFFERS

TOTAL NO. OF SHEETS

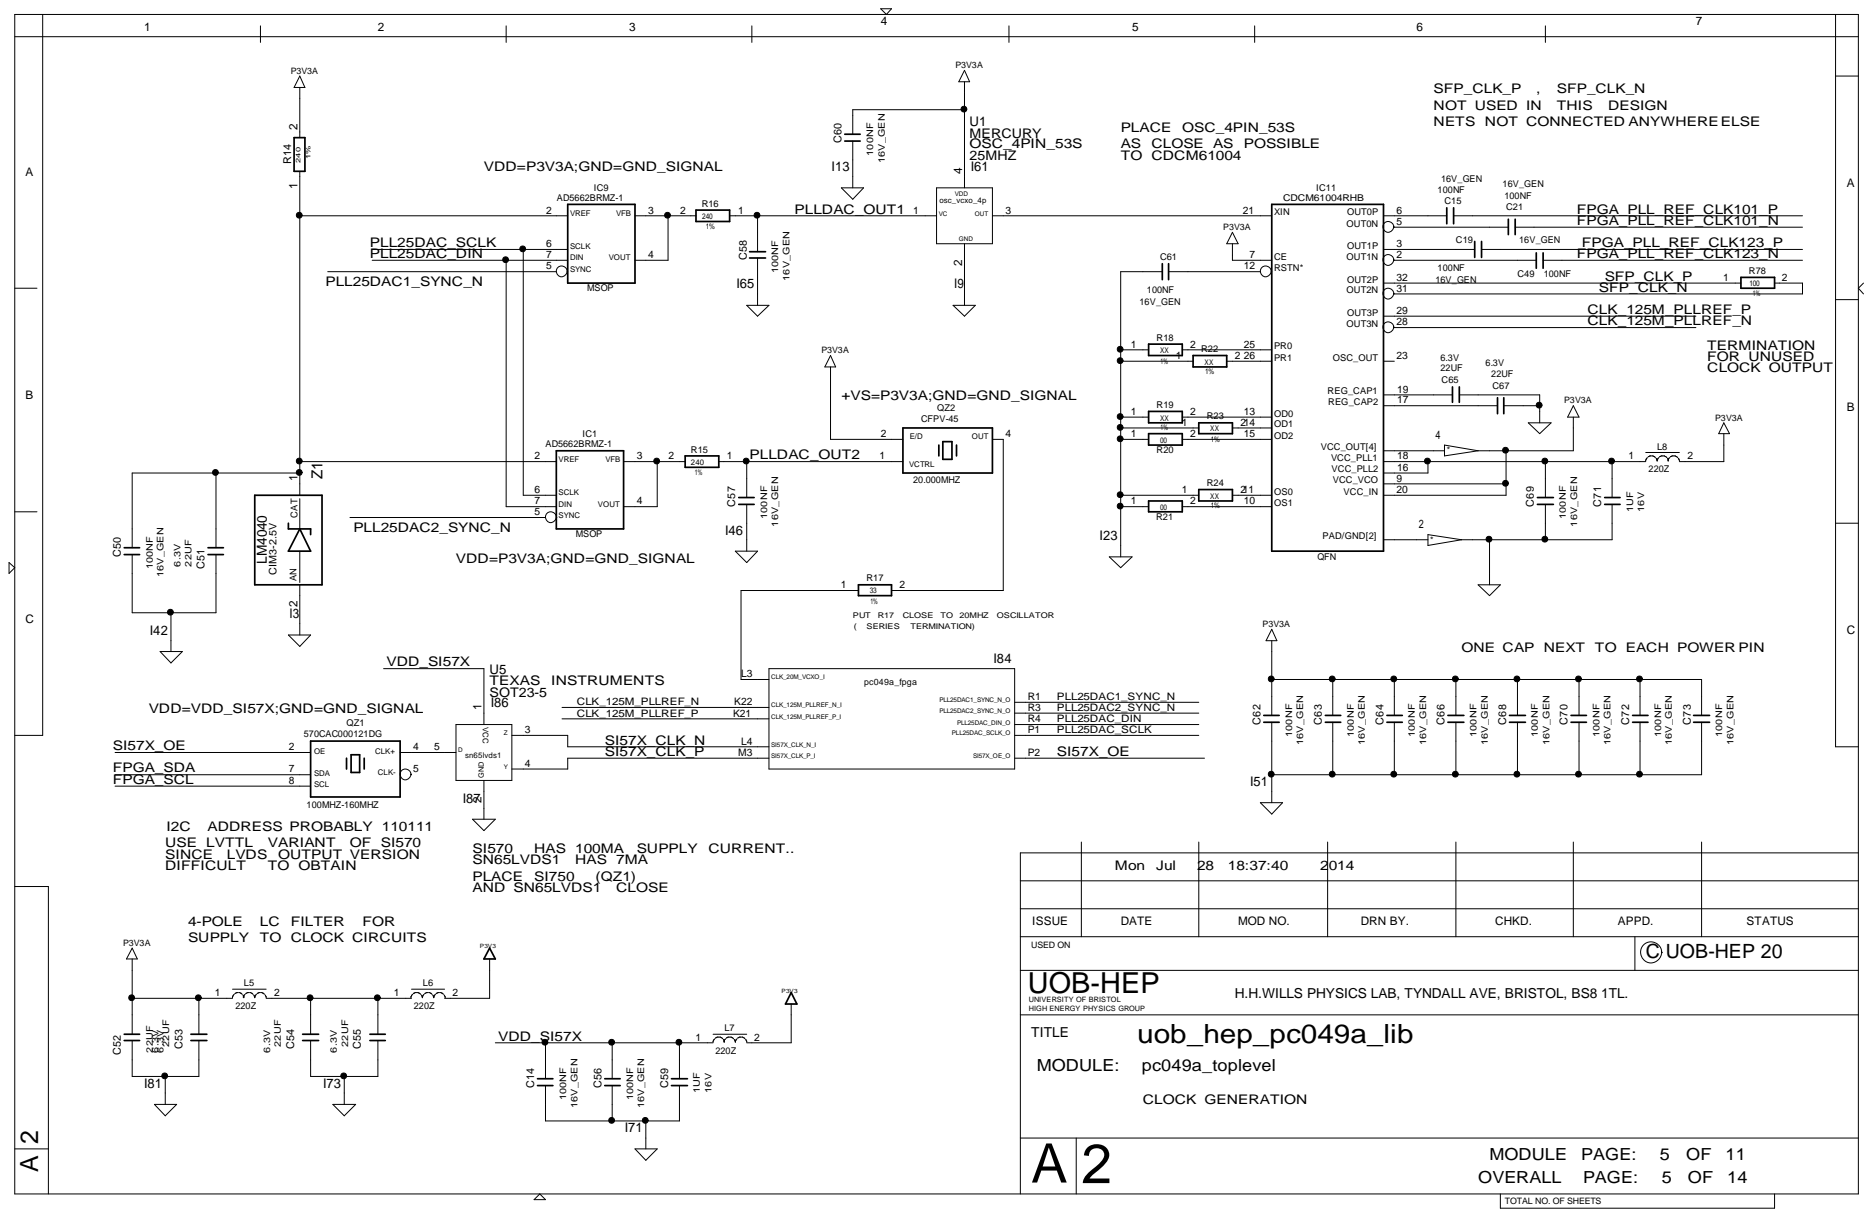
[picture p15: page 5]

SFP_CLK_P , SFP_CLK_N
NOT USED IN THIS DESIGN
NETS NOT CONNECTED ANYWHERE ELSE

PLACE OSC_4PIN_53S
AS CLOSE AS POSSIBLE
TO CDCM61004

ONE CAP NEXT TO EACH POWER PIN

I2C ADDRESS PROBABLY 110111
SINCE LVDS OUTPUT VERSION

4-POLE LC FILTER FOR
SUPPLY TO CLOCK CIRCUITS

ISSUE | DATE | MOD NO. | DRN BY. | CHKD. | APPD. | STATUS

USED ON | C UOB-HEP 20

H.H.WILLS PHYSICS LAB, TYNDALL AVE, BRISTOL, BS8 1TL.

TOTAL NO. OF SHEETS

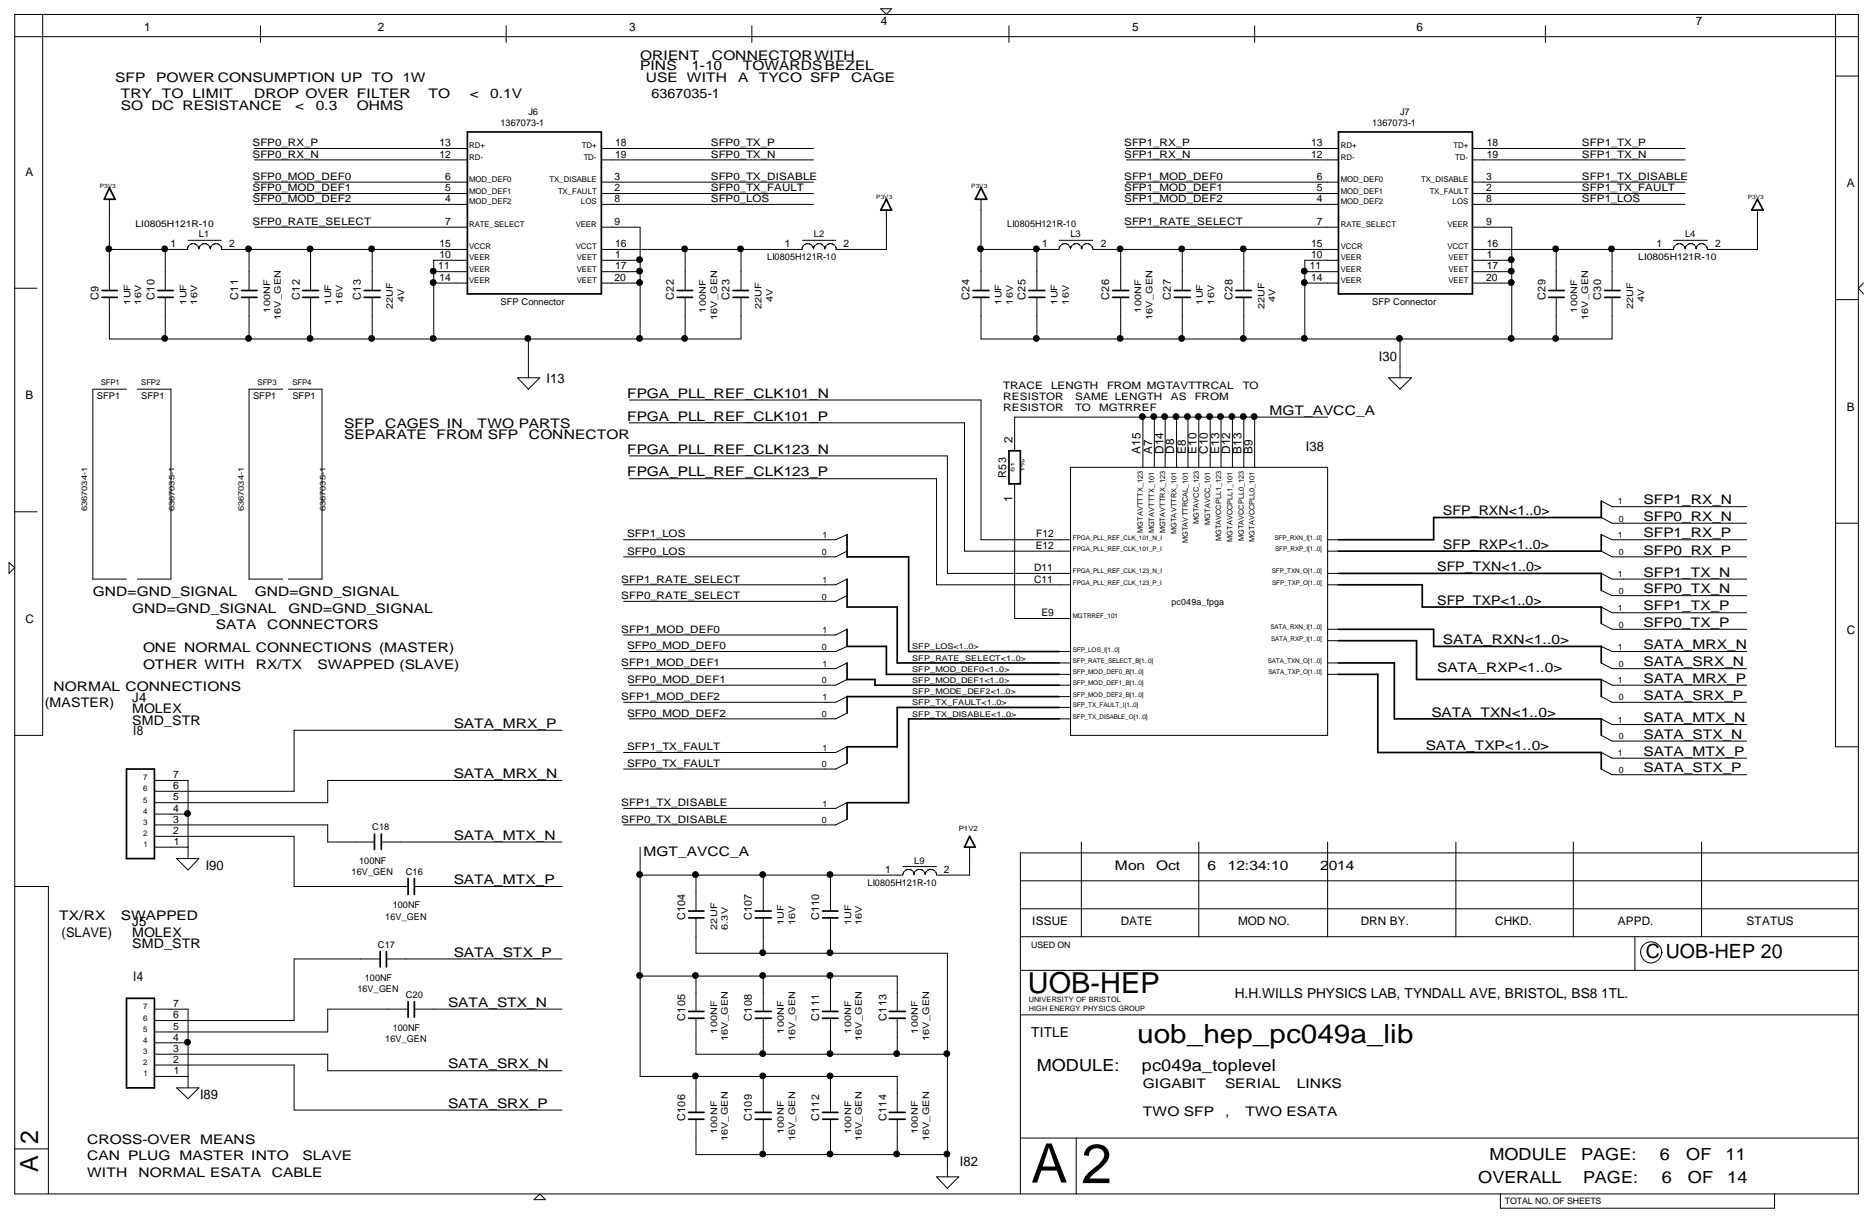
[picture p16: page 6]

ORIENT CONNECTORWITH
USE WITH A TYCO SFP CAGE

SFP POWER CONSUMPTION UP TO 1W

TRACE LENGTH FROM MGTAVTTRCAL TO
RESISTOR SAME LENGTH AS FROM
RESISTOR TO MGTRREF

SFP CAGES IN TWO PARTS
SEPARATE FROM SFP CONNECTOR

ONE NORMAL CONNECTIONS (MASTER)
OTHER WITH RX/TX SWAPPED (SLAVE)

1 | 100NF 16V_GEN

Mon Oct | 6 12:34:10 2014

C107 ISSUE DATE MOD NO. DRN BY. CHKD. APPD. STATUS

H.H.WILLS PHYSICS LAB, TYNDALL AVE, BRISTOL, BS8 1TL.

TWO SFP , TWO ESATA

CROSS-OVER MEANS
CAN PLUG MASTER INTO SLAVE
WITH NORMAL ESATA CABLE

TOTAL NO. OF SHEETS

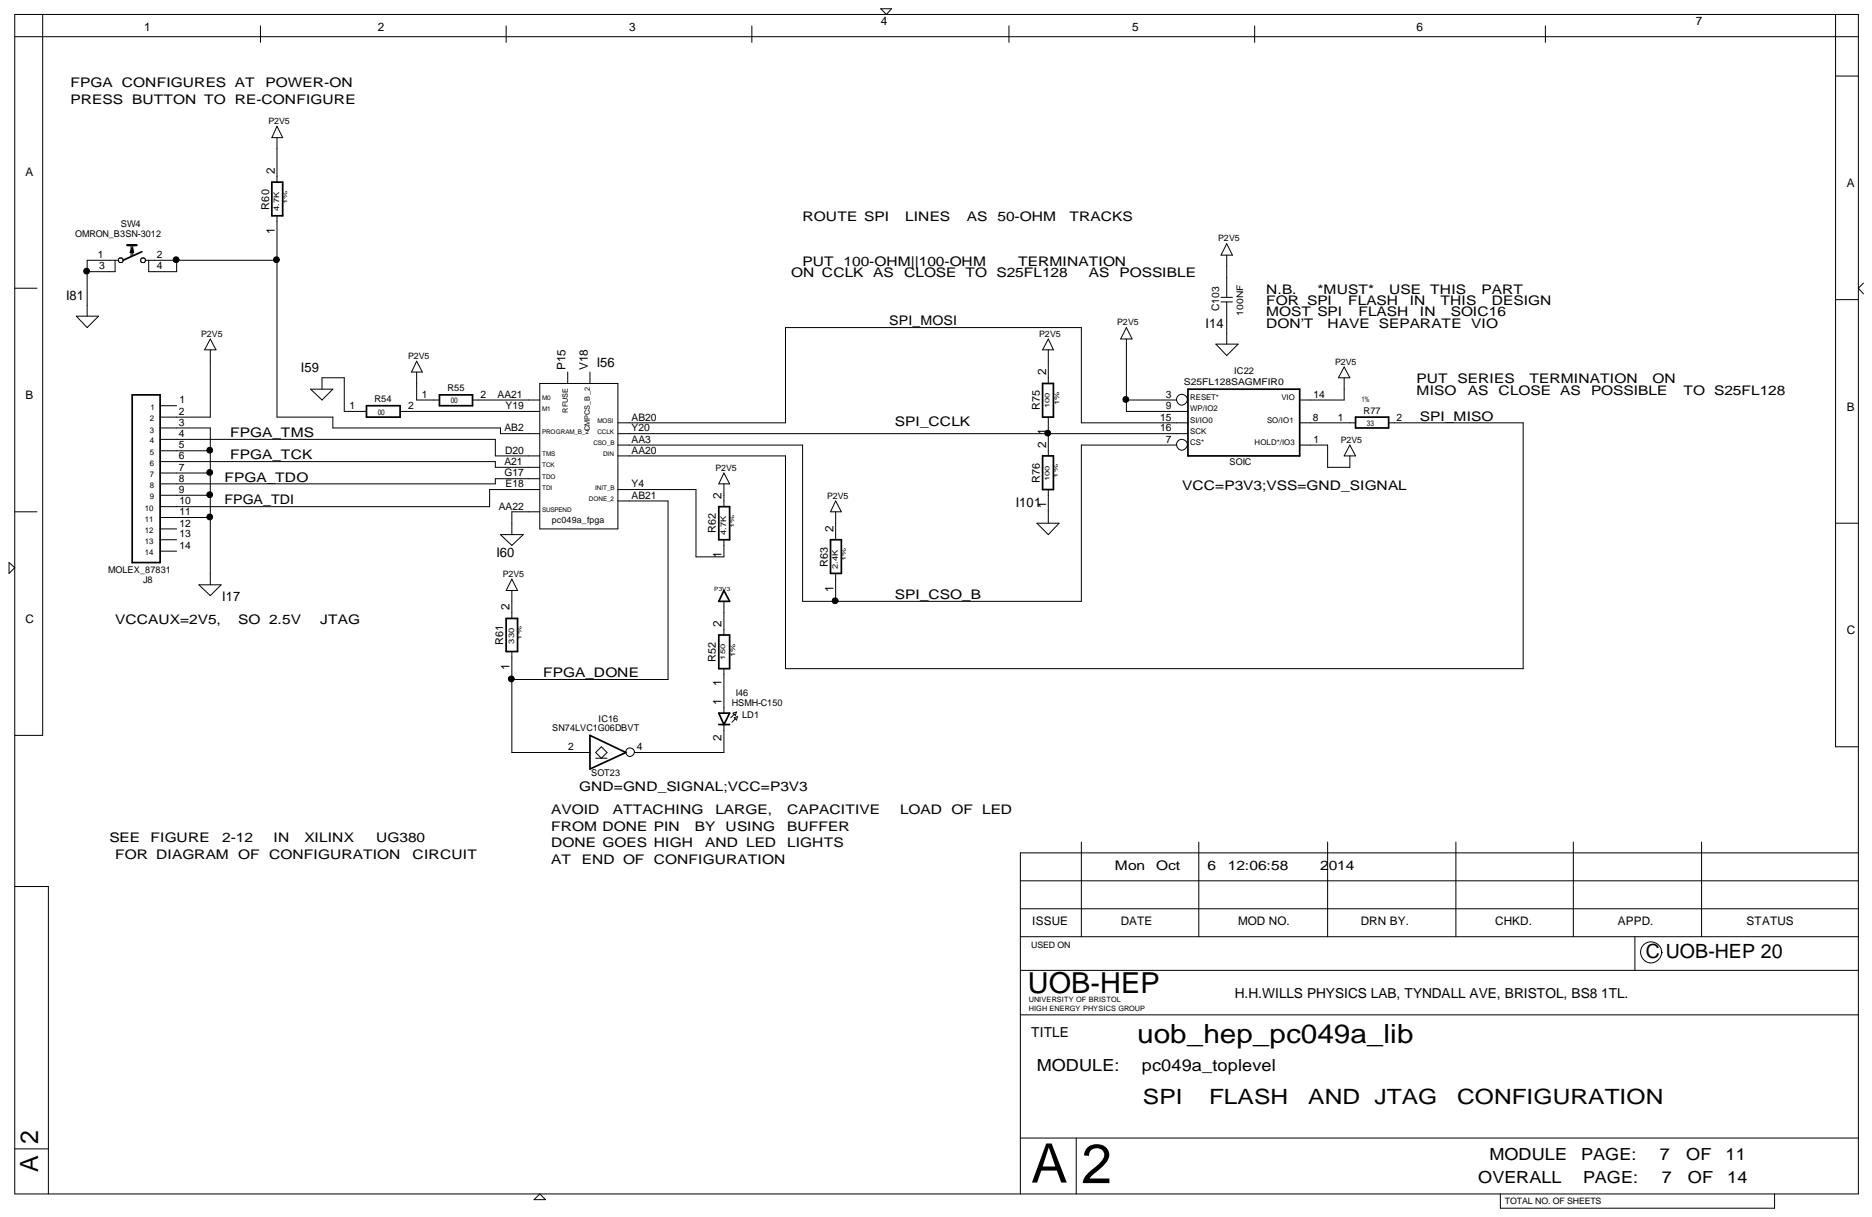
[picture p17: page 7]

FPGA CONFIGURES AT POWER-ON
PRESS BUTTON TO RE-CONFIGURE

ROUTE SPI LINES AS 50-OHM TRACKS

FOR SPI FLASH IN THIS DESIGN
MOST SPI FLASH IN SOIC16
DON’T HAVE SEPARATE VIO

PUT SERIES TERMINATION ON
MISO AS CLOSE AS POSSIBLE TO S25FL128
SPI_MISO

4 | D20 | Y20 AA3 | 16 | 1 P2V5
5 | FPGA_TCK | AA20
6 7 | A21 FPGA_TDO | P2V5
8 | G17 E18 FPGA_TDI | AB21 910

SOT23
GND=GND_SIGNAL;VCC=P3V3
FROM DONE PIN BY USING BUFFER
DONE GOES HIGH AND LED LIGHTS

AT END OF CONFIGURATION FOR DIAGRAM OF CONFIGURATION CIRCUIT

ISSUE | DATE | MOD NO. | DRN BY. | CHKD. | APPD. | STATUS

USED ON | C UOB-HEP 20

H.H.WILLS PHYSICS LAB, TYNDALL AVE, BRISTOL, BS8 1TL.

SPI FLASH AND JTAG CONFIGURATION

TOTAL NO. OF SHEETS

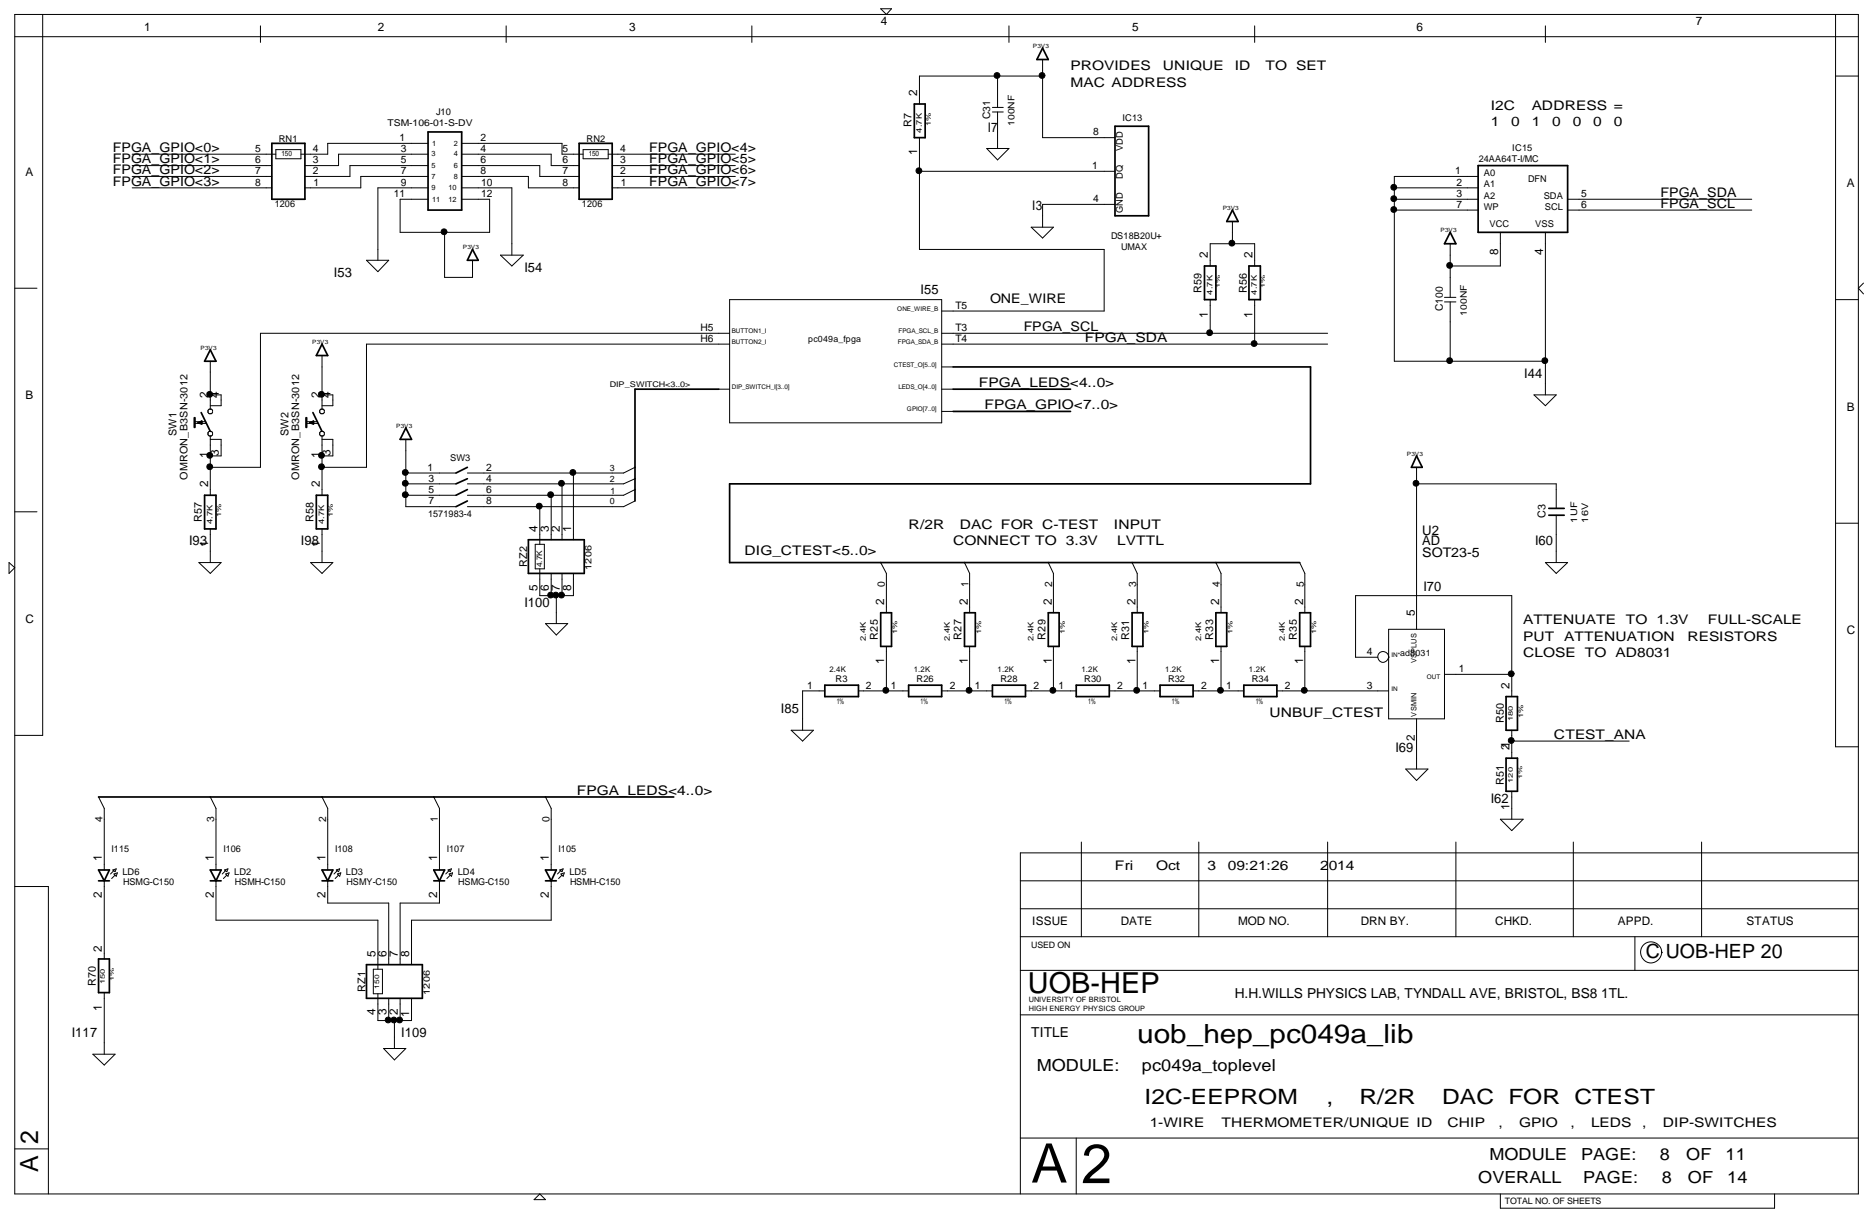
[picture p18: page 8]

PROVIDES UNIQUE ID TO SET
MAC ADDRESS

150 | 3 | 5 | 6 | 6 | 3 FPGA_GPIO<6> FPGA_GPIO<5>

R/2R DAC FOR C-TEST INPUT

ISSUE | DATE | MOD NO. | DRN BY. | CHKD. | APPD. | STATUS

USED ON | C UOB-HEP 20

H.H.WILLS PHYSICS LAB, TYNDALL AVE, BRISTOL, BS8 1TL.

I2C-EEPROM , R/2R DAC FOR CTEST
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

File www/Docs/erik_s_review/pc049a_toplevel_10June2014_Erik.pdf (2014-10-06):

## FPGA CONNECTIONS

# MAROC

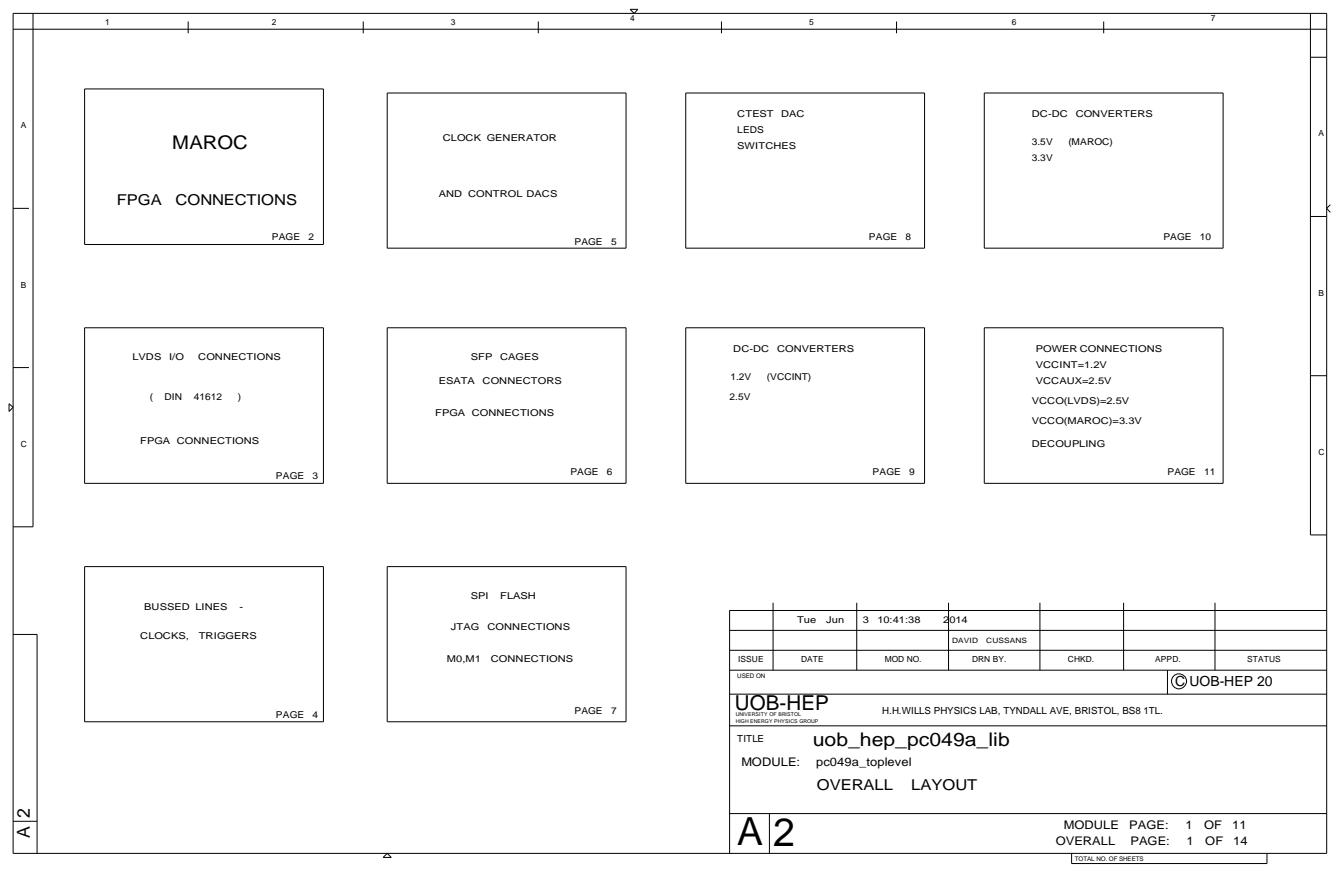
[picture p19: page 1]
OVERALL LAYOUT; PAGE 3; PAGE 4; CLOCKS, TRIGGERS; BUSSED LINES -; ( DIN 41612; LVDS I/O; CONNECTIONS; FPGA CONNECTIONS; PAGE 7; SPI FLASH; M0,M1 CONNECTIONS; JTAG CONNECTIONS; PAGE 10; (MAROC); PAGE 2; PAGE 6; ESATA CONNECTORS; SFP CAGES; CLOCK GENERATOR; PAGE 5; PAGE 8; SWITCHES; LEDS; CTEST DAC; PAGE 11; POWER CONNECTIONS; DECOUPLING; VCCINT=1.2V VCCAUX=2.5V; VCCO(LVDS)=2.5V; VCCO(MAROC)=3.3V; PAGE 9; (VCCINT); OVERALL PAGE:; MODULE PAGE:; uob_hep_pc049a_lib; UOB-HEP

DC-DC CONVERTERS

AND CONTROL DACS

Tue Jun | 3 10:41:38 2014

DAVID CUSSANS

ISSUE | DATE | MOD NO. | DRN BY. | CHKD. | APPD. | STATUS

USED ON | C UOB-HEP 20

UNIVERSITY OF BRISTOL
HIGH ENERGY PHYSICS GROUP
TITLE
MODULE: pc049a_toplevel

H.H.WILLS PHYSICS LAB, TYNDALL AVE, BRISTOL, BS8 1TL.

TOTAL NO. OF SHEETS

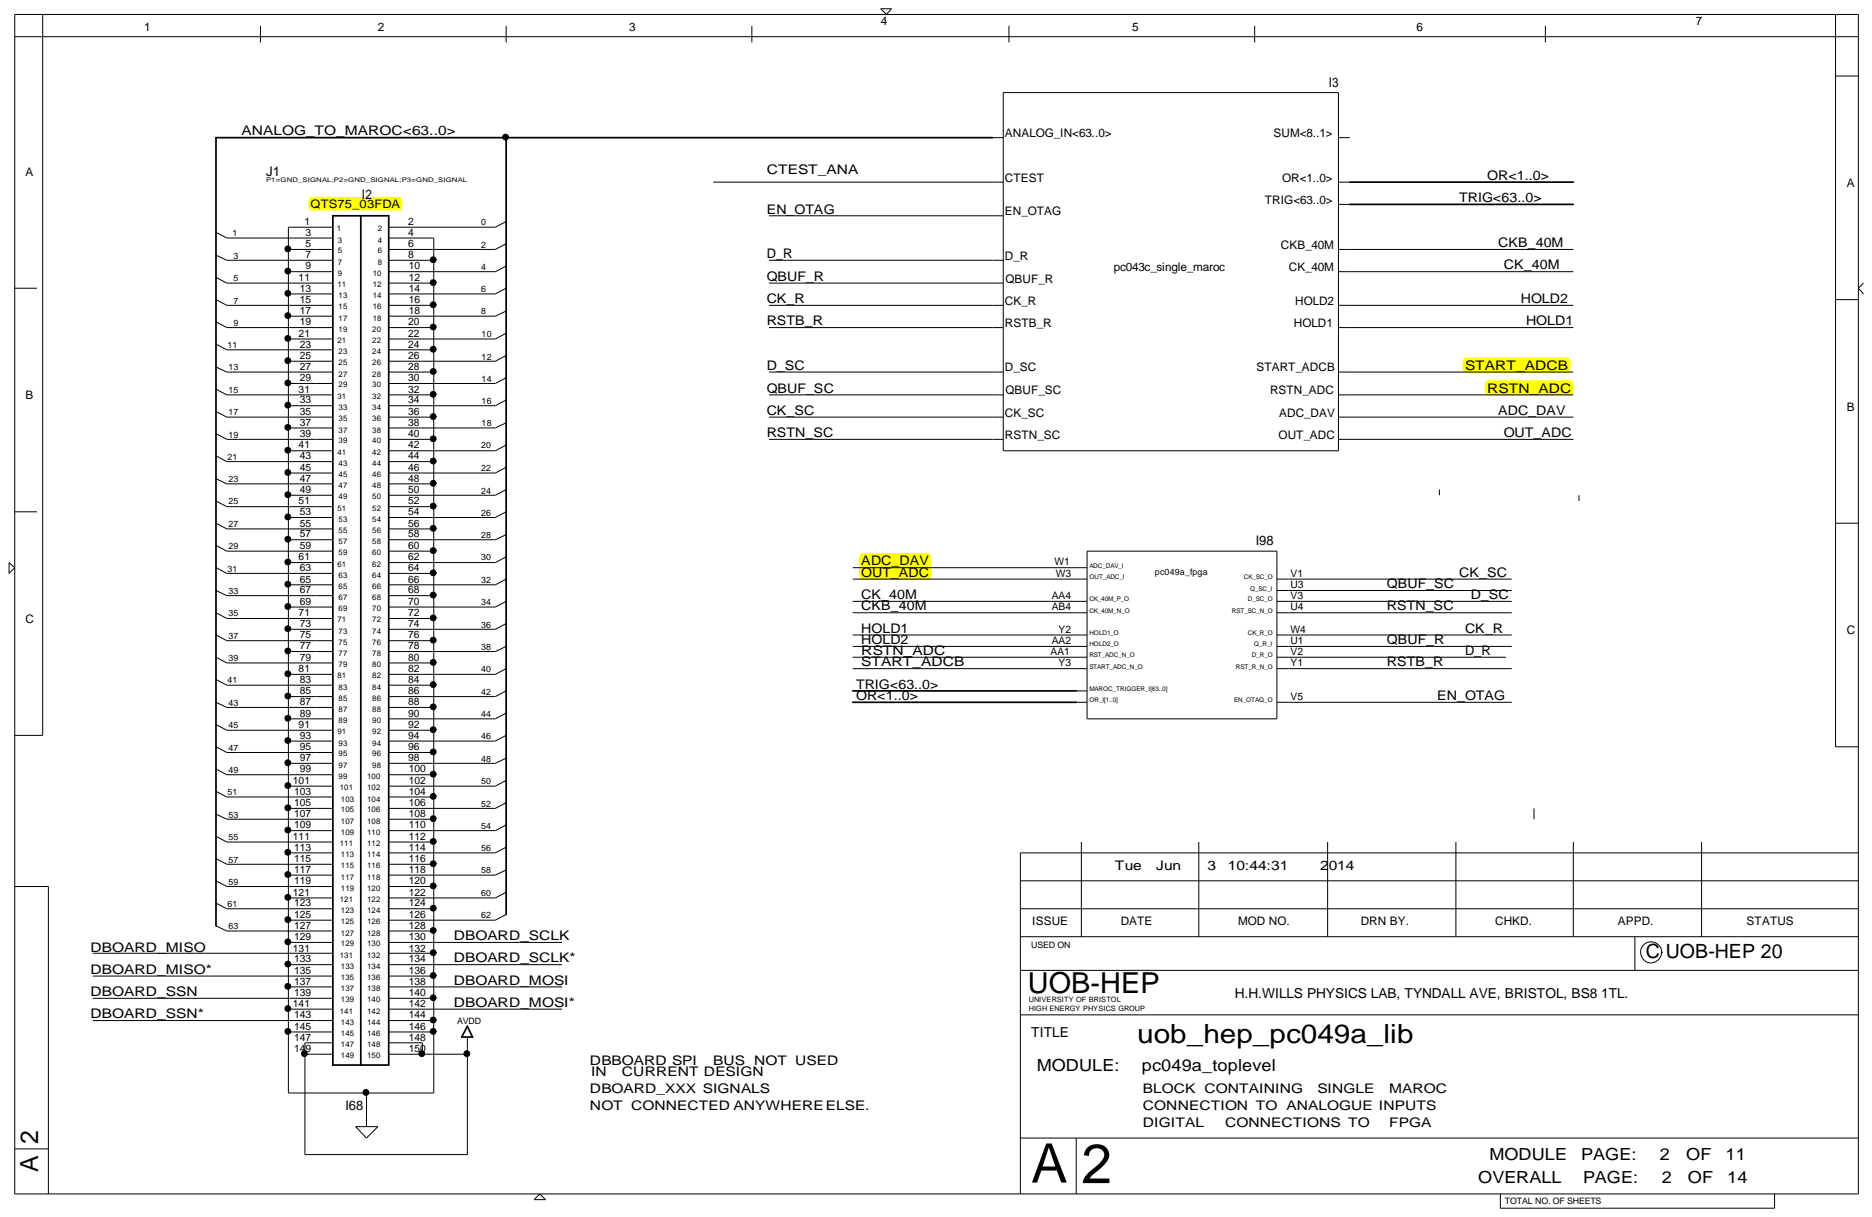
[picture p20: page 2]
DIGITAL; CONNECTIONS TO; FPGA; DBOARD_MOSI; DBOARD_SCLK*; DBOARD_MOSI*; Tue Jun; OVERALL PAGE:; MODULE PAGE:; uob_hep_pc049a_lib; P1=GND_SIGNAL;P2=GND_SIGNAL;P3=GND_SIGNAL; ANALOG_TO_MAROC<63..0>; CTEST_ANA; QBUF_SC; RSTB_R; QBUF_SC RSTN_SC; QBUF_R RSTB_R; EN_OTAG; ADC_DAV OUT_ADC CK_40M CKB_40M HOLD1 HOLD2 RSTN_ADC; TRIG<63..0>; START_ADCB; OR<1..0> TRIG<63..0>; CK_SC RSTN_SC; QBUF_R; START_ADCB RSTN_ADC; HOLD2 HOLD1; CKB_40M; OUT_ADC; ADC_DAV; DBOARD_SCLK; QTS75_03FDA; DBOARD_SSN*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

UNIVERSITY OF BRISTOL
HIGH ENERGY PHYSICS GROUP
TITLE
MODULE: pc049a_toplevel

H.H.WILLS PHYSICS LAB, TYNDALL AVE, BRISTOL, BS8 1TL.

DBBOARD SPI BUS NOT USED
IN CURRENT DESIGN
DBOARD_XXX SIGNALS
NOT CONNECTED ANYWHERE ELSE.

BLOCK CONTAINING SINGLE MAROC
CONNECTION TO ANALOGUE INPUTS

TOTAL NO. OF SHEETS

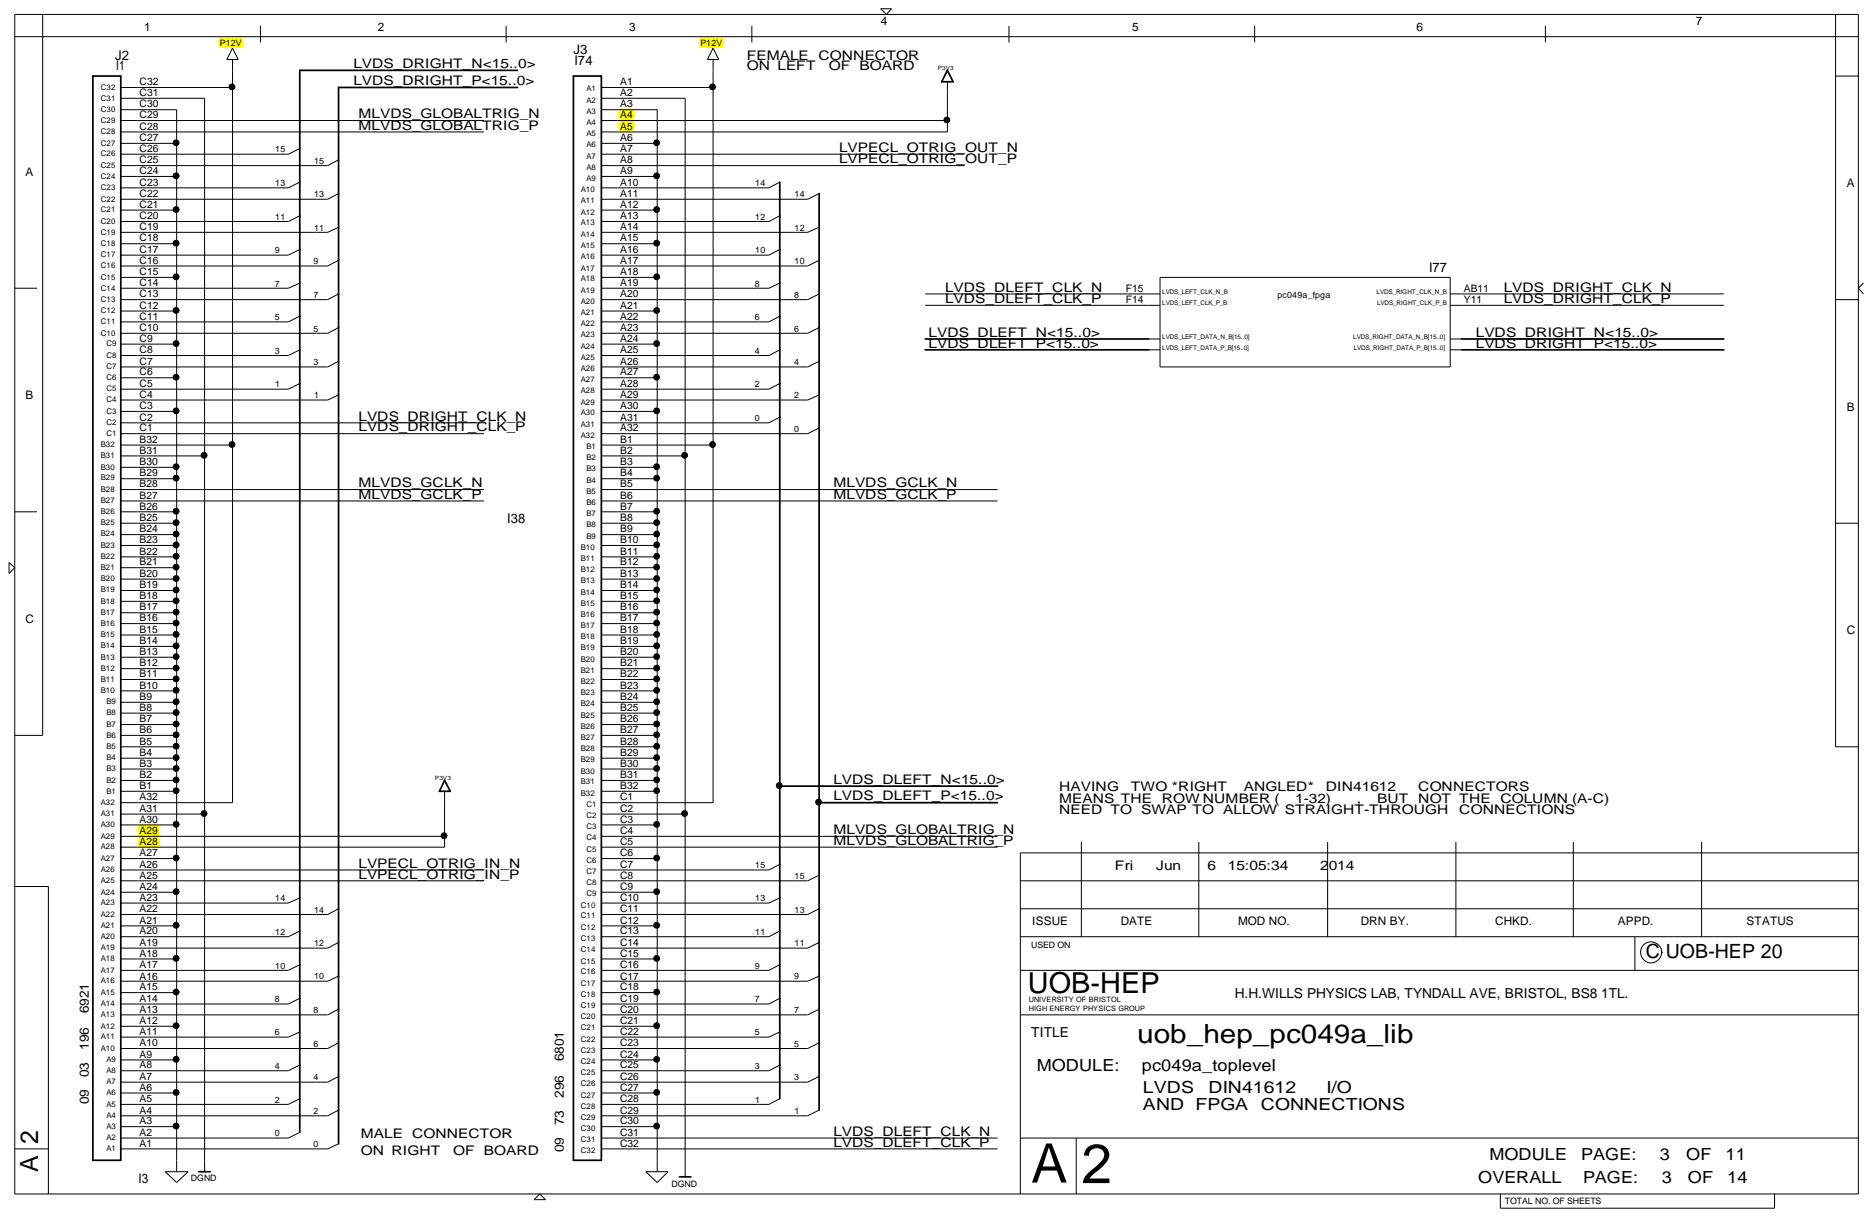
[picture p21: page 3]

A | FEMALE CONNECTOR

ON LEFT OF BOARD

A5
A6

A28
A27

ISSUE | DATE | MOD NO. | DRN BY. | CHKD. | APPD. | STATUS

USED ON | C UOB-HEP 20

H.H.WILLS PHYSICS LAB, TYNDALL AVE, BRISTOL, BS8 1TL.

MALE CONNECTOR
ON RIGHT OF BOARD

TOTAL NO. OF SHEETS

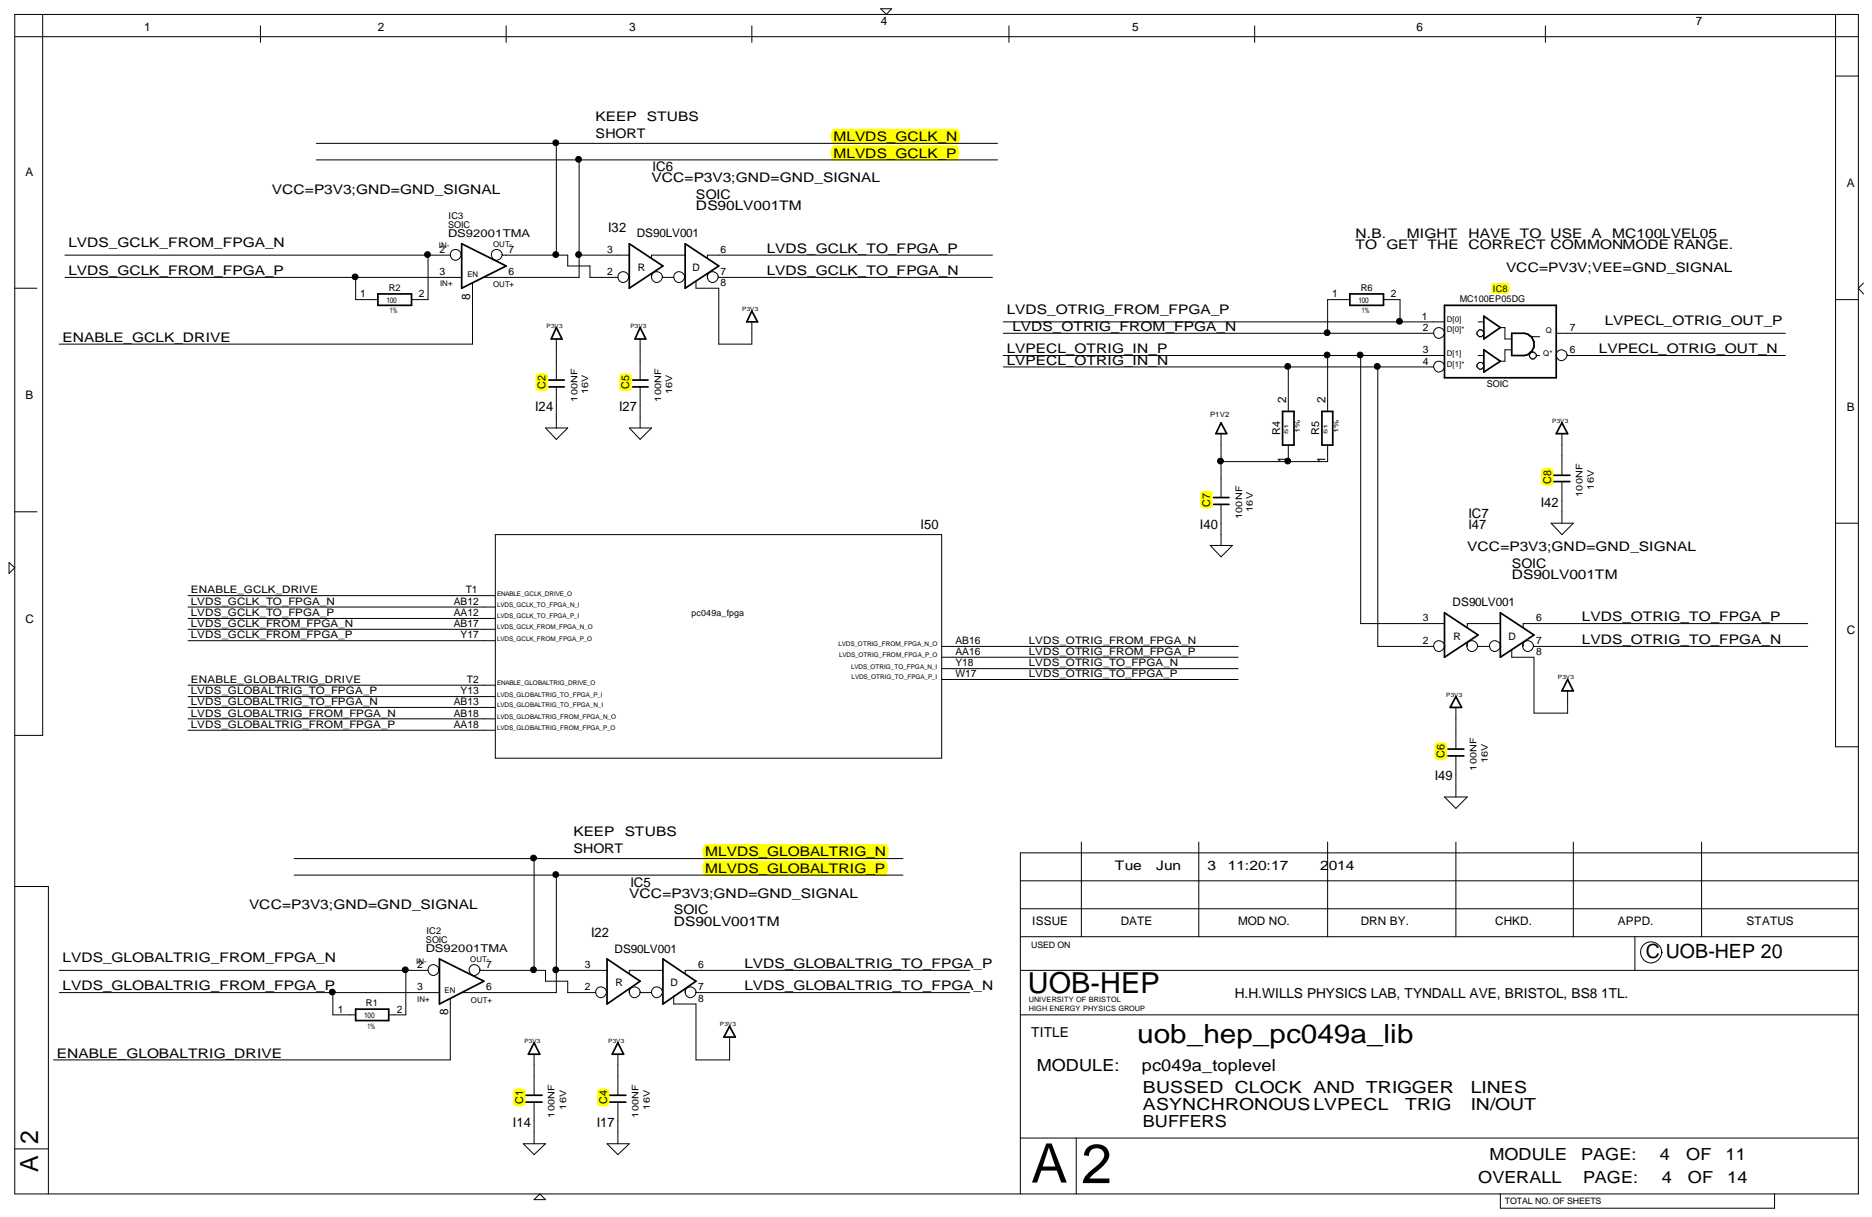
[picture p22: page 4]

VCC=P3V3;GND=GND_SIGNAL

TO GET THE CORRECT COMMONMODE RANGE.

ISSUE | DATE | MOD NO. | DRN BY. | CHKD. | APPD. | STATUS

USED ON | C UOB-HEP 20

H.H.WILLS PHYSICS LAB, TYNDALL AVE, BRISTOL, BS8 1TL.

BUSSED CLOCK AND TRIGGER LINES
ASYNCHRONOUS LVPECL TRIG IN/OUT
BUFFERS

TOTAL NO. OF SHEETS


SFP_CLK_P , SFP_CLK_N
NOT USED IN THIS DESIGN
NETS NOT CONNECTED ANYWHERE ELSE

ONE CAP NEXT TO EACH POWER PIN

4-POLE LC FILTER FOR
SUPPLY TO CLOCK CIRCUITS

ISSUE | DATE | MOD NO. | DRN BY. | CHKD. | APPD. | STATUS

USED ON | C UOB-HEP 20

H.H.WILLS PHYSICS LAB, TYNDALL AVE, BRISTOL, BS8 1TL.

TOTAL NO. OF SHEETS


TRACE LENGTH FROM MGTAVTTRCAL TO
RESISTOR SAME LENGTH AS FROM
RESISTOR TO MGTRREF

SFP CAGES IN TWO PARTS
SEPARATE FROM SFP CONNECTOR

ONE NORMAL CONNECTIONS (MASTER)
OTHER WITH RX/TX SWAPPED (SLAVE)

Thu Jun | 5 09:13:02 2014

ISSUE | DATE | MOD NO. | DRN BY. | CHKD. | APPD. | STATUS

USED ON | C UOB-HEP 20

H.H.WILLS PHYSICS LAB, TYNDALL AVE, BRISTOL, BS8 1TL.

1 | 100NF

TWO SFP , TWO ESATA

CROSS-OVER MEANS
CAN PLUG MASTER INTO SLAVE
WITH NORMAL ESATA CABLE

TOTAL NO. OF SHEETS


FPGA CONFIGURES AT POWER-ON
PRESS BUTTON TO RE-CONFIGURE

ROUTE SPI LINES AS 50-OHM TRACKS

FOR SPI FLASH IN THIS DESIGN
MOST SPI FLASH IN SOIC16
DON’T HAVE SEPARATE VIO

PUT SERIES TERMINATION ON
MISO AS CLOSE AS POSSIBLE TO S25FL128
SPI_MISO

4 | D20 | Y20 AA3 | 16 | 1 P2V5
5 | FPGA_TCK | AA20
6 7 | A21 FPGA_TDO | P2V5
8 | G17 E18 FPGA_TDI | AB21 910

FROM DONE PIN BY USING BUFFER
DONE GOES HIGH AND LED LIGHTS

ISSUE | DATE | MOD NO. | DRN BY. | CHKD. | APPD. | STATUS

USED ON | C UOB-HEP 20

H.H.WILLS PHYSICS LAB, TYNDALL AVE, BRISTOL, BS8 1TL.

SPI FLASH AND JTAG CONFIGURATION

TOTAL NO. OF SHEETS


PROVIDES UNIQUE ID TO SET
MAC ADDRESS

150 1% | 6 | 5 | 6 | 3 | 6 FPGA_GPIO<5> FPGA_GPIO<6> ¹%

R/2R DAC FOR C-TEST INPUT

ISSUE | DATE | MOD NO. | DRN BY. | CHKD. | APPD. | STATUS

USED ON | C UOB-HEP 20

H.H.WILLS PHYSICS LAB, TYNDALL AVE, BRISTOL, BS8 1TL.

I2C-EEPROM , R/2R DAC FOR CTEST

1-WIRE THERMOMETER/UNIQUE ID CHIP , GPIO , LEDS , DIP-SWITCHES

TOTAL NO. OF SHEETS


WANT TO KEEP GROUND AND POWER-PLANE NOISE AWAY FROM MAROC
PUT FILTER BETWEEN GROUND PLANE OF DC-DC CONVERTER
AND GROUND PLANE OF REST OF BOARD

PUT LINEAR REGULATOR NEAR FPGA

AIM FOR VERY LOW CSR CAPS ON VD

ROUTE BETWEEN BNX002 AND
REGULATOR WITH 5MM WIDE TRACK

ISSUE | DATE | MOD NO. | DRN BY. | CHKD. | APPD. | STATUS
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

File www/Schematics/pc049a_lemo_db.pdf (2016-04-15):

Thu May; OVERALL; PAGE: 1 OF 18; MODULE; PAGE: 1 OF 2; uob_hep_pc049a_lib; MODULE:; DBOARD_SCLK* DBOARD_MOSI DBOARD_MOSI*; P1=GND_SIGNAL;P2=GND_SIGNAL;P3=GND_SIGNAL; DBOARD_SSN DBOARD_SSN*; ANALOG_TO_MAROC<63..0>; DBOARD_SCLK; I35 QSS75_01FDA; DBOARD_MISO*; DBOARD_MISO; USED ON; AVDD; ISSUE; DATE; MOD NO.; DRN BY.; CHKD.; APPD.; STATUS; C UOB-HEP 20; UOB-HEP

UNIVERSITY OF BRISTOL
HIGH ENERGY PHYSICS GROUP
TITLE

H.H.WILLS PHYSICS LAB, TYNDALL AVE, BRISTOL, BS8 1TL.

CONNECT UP LINES THAT
COULD BE USED FOR AN SPI BUS
ON LVDS.
COULD ALSO USE
AS I2C WITH APPROPRIATE LEVEL
TRANSLATION

TOTAL NO. OF SHEETS

Mon Mar 17 15:31:35 2014; OVERALL; PAGE: 2 OF 18; MODULE; PAGE: 2 OF 2; uob_hep_pc049a_lib; MODULE:; LEMO_GRP_M<3..0>; ANALOG_TO_MAROC<63..0>; LEMO_GRP_N<3..0>; LEMO_GRP_L<3..0>; LEMO_GRP_K<3..0>; LEMO_GRP_J<3..0>; LEMO_GRP_I<3..0>; LEMO_GRP_P<3..0>; LEMO_GRP_O<3..0>; LEMO_GRP_A<3..0>; LEMO_GRP_B<3..0>; LEMO_GRP_C<3..0>; LEMO_GRP_D<3..0>; LEMO_GRP_E<3..0>; LEMO_GRP_F<3..0>; LEMO_GRP_G<3..0>; LEMO_GRP_H<3..0>; PC049A_4LEMOS; ANALOG_IN<3..0>; UOB-HEP

ISSUE | DATE | MOD NO. | DRN BY. | CHKD. | APPD. | STATUS

USED ON | C UOB-HEP 20

UNIVERSITY OF BRISTOL
HIGH ENERGY PHYSICS GROUP
TITLE

H.H.WILLS PHYSICS LAB, TYNDALL AVE, BRISTOL, BS8 1TL.

TOTAL NO. OF SHEETS

AND; DC BLOCKING CAPACITORS; FOUR; LEMO CONNECTORS WITH; ESD; PROTECTION; OVERALL; PAGE: 3 OF 18; MODULE; PAGE: 1 OF 1; uob_hep_pc049a_lib; MODULE:; pc049a_4lemos; SP3010-04UTG; PLEMO00D; UDFN; ANALOG_IN<3..0>; OUT; UOB-HEP

MAROC INPUTS ARE BIASED TO ABOUT 700MV
DC-PATH TO GROUND ( E.G. EXTERNAL TERMINATION)
CAUSES PROBLEMS.
ADD CAPACITORS TO PROVIDE DC-BLOCK

ESD PROTECTION TO PROTECT MAROCS

2 | 180 | 7 | | | 2

DC PATH TO GROUND

Wed May | 7 15:21:30 2014

D. CUSSANS

ISSUE | DATE | MOD NO. | DRN BY. | CHKD. | APPD. | STATUS
USED ON | C UOB-HEP 20 14

UNIVERSITY OF BRISTOL
HIGH ENERGY PHYSICS GROUP
TITLE

H.H.WILLS PHYSICS LAB, TYNDALL AVE, BRISTOL, BS8 1TL.

TOTAL NO. OF SHEETS



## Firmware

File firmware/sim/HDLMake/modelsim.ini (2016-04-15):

; vsim modelsim.ini file, version 10.4
[Version]
INIVersion = 10.4

; Copyright 1991-2014 Mentor Graphics Corporation
;
; All Rights Reserved.
;
; THIS WORK CONTAINS TRADE SECRET AND PROPRIETARY INFORMATION WHICH IS THE PROPERTY OF 
; MENTOR GRAPHICS CORPORATION OR ITS LICENSORS AND IS SUBJECT TO LICENSE TERMS.
;   

[Library]
std = $MODEL_TECH/../std
ieee = $MODEL_TECH/../ieee
vital2000 = $MODEL_TECH/../vital2000
;
; VITAL concerns:
;
; The library ieee contains (among other packages) the packages of the
; VITAL 2000 standard.  When a design uses VITAL 2000 exclusively, it should use
; the physical library ieee (recommended), or use the physical library
; vital2000, but not both.  The design can use logical library ieee and/or
; vital2000 as long as each of these maps to the same physical library, either
; ieee or vital2000.
;
; A design using the 1995 version of the VITAL packages, whether or not
; it also uses the 2000 version of the VITAL packages, must have logical library
; name ieee mapped to physical library vital1995.  (A design cannot use library
; vital1995 directly because some packages in this library use logical name ieee
; when referring to the other packages in the library.)  The design source
; should use logical name ieee when referring to any packages there except the
; VITAL 2000 packages.  Any VITAL 2000 present in the design must use logical
; name vital2000 (mapped to physical library vital2000) to refer to those
; packages.
; ieee = $MODEL_TECH/../vital1995
;
; For compatiblity with previous releases, logical library name vital2000 maps
; to library vital2000 (a different library than library ieee, containing the
; same packages).
; A design should not reference VITAL from both the ieee library and the
; vital2000 library because the vital packages are effectively different.
; A design that references both the ieee and vital2000 libraries must have
; both logical names ieee and vital2000 mapped to the same library, either of
; these:
;   $MODEL_TECH/../ieee
;   $MODEL_TECH/../vital2000
;
verilog = $MODEL_TECH/../verilog
std_developerskit = $MODEL_TECH/../std_developerskit
synopsys = $MODEL_TECH/../synopsys
modelsim_lib = $MODEL_TECH/../modelsim_lib
sv_std = $MODEL_TECH/../sv_std
mtiAvm = $MODEL_TECH/../avm
mtiRnm = $MODEL_TECH/../rnm
mtiOvm = $MODEL_TECH/../ovm-2.1.2
mtiUvm = $MODEL_TECH/../uvm-1.1d
mtiUPF = $MODEL_TECH/../upf_lib
mtiPA  = $MODEL_TECH/../pa_lib
floatfixlib = $MODEL_TECH/../floatfixlib
mc2_lib = $MODEL_TECH/../mc2_lib
osvvm = $MODEL_TECH/../osvvm

; added mapping for ADMS
mgc_ams = $MODEL_TECH/../mgc_ams
ieee_env = $MODEL_TECH/../ieee_env

;vhdl_psl_checkers = $MODEL_TECH/../vhdl_psl_checkers       // Source files only for this release
;verilog_psl_checkers = $MODEL_TECH/../verilog_psl_checkers // Source files only for this release
;mvc_lib = $MODEL_TECH/../mvc_lib
infact = $MODEL_TECH/../infact

secureip = /software/CAD/Xilinx/14.7_64b/14.7/ISE_DS/ISE/verilog/questasim/10.2c_5/lin64//secureip
unimacro = /software/CAD/Xilinx/14.7_64b/14.7/ISE_DS/ISE/vhdl/questasim/10.2c_5/lin64//unimacro
unisim = /software/CAD/Xilinx/14.7_64b/14.7/ISE_DS/ISE/vhdl/questasim/10.2c_5/lin64//unisim
xilinxcorelib = /software/CAD/Xilinx/14.7_64b/14.7/ISE_DS/ISE/vhdl/questasim/10.2c_5/lin64//xilinxcorelib


[DefineOptionset]
; Define optionset entries for the various compilers, vmake, and vsim.
; These option sets can be used with the "-optionset <optionsetname>" syntax.
; i.e.
;  vlog -optionset COMPILEDEBUG top.sv
;  vsim -optionset UVMDEBUG my_top
;
; Following are some useful examples.

; define a vsim optionset for uvm debugging
UVMDEBUG = -uvmcontrol=all -msgmode both -displaymsgmode both -classdebug -onfinish stop

; define a vopt optionset for debugging
VOPTDEBUG = +acc -debugdb


[vcom]
; VHDL93 variable selects language version as the default. 
; Default is VHDL-2002.
; Value of 0 or 1987 for VHDL-1987.
; Value of 1 or 1993 for VHDL-1993.
; Default or value of 2 or 2002 for VHDL-2002.
; Value of 3 or 2008 for VHDL-2008
; Value of 4 or ams99 for VHDL-AMS-1999
; Value of 5 or ams07 for VHDL-AMS-2007
VHDL93 = 2002

; Ignore VHDL-2008 declaration of REAL_VECTOR in package STANDARD. Default is off.
; ignoreStandardRealVector = 1

; Show source line containing error. Default is off.
; Show_source = 1

; Turn off unbound-component warnings. Default is on.
; Show_Warning1 = 0

; Turn off process-without-a-wait-statement warnings. Default is on.
; Show_Warning2 = 0

; Turn off null-range warnings. Default is on.
; Show_Warning3 = 0

; Turn off no-space-in-time-literal warnings. Default is on.
; Show_Warning4 = 0

; Turn off multiple-drivers-on-unresolved-signal warnings. Default is on.
; Show_Warning5 = 0

; Turn off optimization for IEEE std_logic_1164 package. Default is on.
; Optimize_1164 = 0

; Enable compiler statistics. Specify one or more arguments: 
;                   [all,none,time,cmd,msg,perf,verbose,list]
; Add '-' to disable specific statistics. Default is [time,cmd,msg].
; Stats = time,cmd,msg

; Turn on resolving of ambiguous function overloading in favor of the
; "explicit" function declaration (not the one automatically created by
; the compiler for each type declaration). Default is off.
; The .ini file has Explicit enabled so that std_logic_signed/unsigned
; will match the behavior of synthesis tools.
Explicit = 1

; Turn off acceleration of the VITAL packages. Default is to accelerate.
; NoVital = 1

; Turn off VITAL compliance checking. Default is checking on.
; NoVitalCheck = 1

; Ignore VITAL compliance checking errors. Default is to not ignore.
; IgnoreVitalErrors = 1

; Turn off VITAL compliance checking warnings. Default is to show warnings.
; Show_VitalChecksWarnings = 0

; Turn off PSL assertion warning messages. Default is to show warnings.
; Show_PslChecksWarnings = 0

; Enable parsing of embedded PSL assertions. Default is enabled.
; EmbeddedPsl = 0

; Keep silent about case statement static warnings.
; Default is to give a warning.
; NoCaseStaticError = 1

; Keep silent about warnings caused by aggregates that are not locally static.
; Default is to give a warning.
; NoOthersStaticError = 1

; Treat as errors:
;   case statement static warnings
;   warnings caused by aggregates that are not locally static
; Overrides NoCaseStaticError, NoOthersStaticError settings.
; PedanticErrors = 1

; Turn off inclusion of debugging info within design units.
; Default is to include debugging info.
; NoDebug = 1

; Turn off "Loading..." messages. Default is messages on.
; Quiet = 1

; Turn on some limited synthesis rule compliance checking. Checks only:
;    -- signals used (read) by a process must be in the sensitivity list
; CheckSynthesis = 1

; Activate optimizations on expressions that do not involve signals,
; waits, or function/procedure/task invocations. Default is off.
; ScalarOpts = 1

; Turns on lint-style checking.
; Show_Lint = 1

; Require the user to specify a configuration for all bindings,
; and do not generate a compile time default binding for the
; component. This will result in an elaboration error of
; 'component not bound' if the user fails to do so. Avoids the rare
; issue of a false dependency upon the unused default binding.
; RequireConfigForAllDefaultBinding = 1

; Perform default binding at compile time.
; Default is to do default binding at load time.
; BindAtCompile = 1;

; Inhibit range checking on subscripts of arrays. Range checking on
; scalars defined with subtypes is inhibited by default.
; NoIndexCheck = 1

; Inhibit range checks on all (implicit and explicit) assignments to
; scalar objects defined with subtypes.
; NoRangeCheck = 1

; Set the prefix to be honored for synthesis/coverage pragma recognition.
; Default is "".
; AddPragmaPrefix = ""

; Ignore synthesis and coverage pragmas with this prefix.
; Default is "".
; IgnorePragmaPrefix = ""

; Turn on code coverage in VHDL design units. Default is off.
; Coverage = sbceft

; Turn off code coverage in VHDL subprograms. Default is on.
; CoverSub = 0

; Automatically exclude VHDL case statement OTHERS choice branches.
; This includes OTHERS choices in selected signal assigment statements.
; Default is to not exclude.
; CoverExcludeDefault = 1

; Control compiler and VOPT optimizations that are allowed when
; code coverage is on.  Refer to the comment for this in the [vlog] area. 
; CoverOpt = 3

; Turn on or off clkOpt optimization for code coverage. Default is on.
; CoverClkOpt = 1

; Turn on or off clkOpt optimization builtins for code coverage. Default is on.
; CoverClkOptBuiltins = 0

; Inform code coverage optimizations to respect VHDL 'H' and 'L'
; values on signals in conditions and expressions, and to not automatically
; convert them to '1' and '0'. Default is to not convert.
; CoverRespectHandL = 0

; Increase or decrease the maximum number of rows allowed in a UDP table
; implementing a VHDL condition coverage or expression coverage expression.
; More rows leads to a longer compile time, but more expressions covered.
; CoverMaxUDPRows = 192

; Increase or decrease the maximum number of input patterns that are present
; in FEC table. This leads to a longer compile time with more expressions
; covered with FEC metric.
; CoverMaxFECRows = 192

; Increase or decrease the limit on the size of expressions and conditions
; considered for expression and condition coverages. Higher FecUdpEffort leads 
; to higher compile, optimize and simulation time, but more expressions and 
; conditions are considered for coverage in the design. FecUdpEffort can
; be set to a number ranging from 1 (low) to 3 (high), defined as:
;   1 - (low) Only small expressions and conditions considered for coverage.
;   2 - (medium) Bigger expressions and conditions considered for coverage.
;   3 - (high) Very large expressions and conditions considered for coverage.
; The default setting is 1 (low).
; FecUdpEffort = 1

; Enable or disable Focused Expression Coverage analysis for conditions and
; expressions. Focused Expression Coverage data is provided by default when
; expression and/or condition coverage is active.
; CoverFEC = 0

; Enable or disable UDP Coverage analysis for conditions and expressions.
; UDP Coverage data is disabled by default when expression and/or condition
; coverage is active.
; CoverUDP = 1

; Enable or disable Rapid Expression Coverage mode for conditions and expressions.
; Disabling this would convert non-masking conditions in FEC tables to matching
; input patterns. 
; CoverREC = 1

; Enable or disable bit-blasting multi-bit operands of reduction prefix expressions
; for expression/condition coverage.
; NOTE: Enabling this may have a negative impact on simulation performance.
; CoverExpandReductionPrefix = 0

; Enable or disable short circuit evaluation of conditions and expressions when
; condition or expression coverage is active. Short circuit evaluation is enabled
; by default.
; CoverShortCircuit = 0

; Enable code coverage reporting of code that has been optimized away.
; The default is not to report.
; CoverReportCancelled = 1

; Enable deglitching of code coverage in combinatorial, non-clocked, processes.
; Default is no deglitching.
; CoverDeglitchOn = 1

; Control the code coverage deglitching period. A period of 0, eliminates delta
; cycle glitches. The value of CoverDeglitchPeriod needs to be either be 0 or a
; time string that includes time units. Examples: 0 or 10.0ps or "10.0 ps".
; CoverDeglitchPeriod = 0

; Use this directory for compiler temporary files instead of "work/_temp"
; CompilerTempDir = /tmp

; Set this to cause the compilers to force data to be committed to disk
; when the files are closed.
; SyncCompilerFiles = 1

; Add VHDL-AMS declarations to package STANDARD
; Default is not to add
; AmsStandard = 1
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

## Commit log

2014-03-14 * Copied single_maroc schematic and layout from pc043
    * Started to construct top level schematic
    * Added some block diagrams
    [BSTPLC.brd, page1.csv, page2.csv, page3.csv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]
2014-03-14 Adding specification for expansion connectors
    [pc049a_digital_signal_connectors.xlsx]
2014-07-25 Adding schematic files before implementing Erik S. suggestions
    [chips.prt, fpga_pinout.xlsx, page1.csv, page10.csv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]
2014-07-25 Adding last of PCB files and some of firmware
2014-07-29 Checking in files after doing most of Erik S's changes
    [chips.prt, netlist_dialcnet.xlsx, netlist_dialcnet_old1.xlsx, page1.csv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]
2014-10-06 Committing design before importing from latest *.brd file
    [02_09_2014_pc049a_toplevel_36_a16-5.brd, 05_10_2014_pc049a_toplevel_39_a16-5.brd, page10.csv, page11.csv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]
2014-10-06 New schematic ( minor bug fixes. Connect SFP cages to ground, connect IC16 power pins correctly
    [pc049a_summary_Erik.xls, pc049a_summary_Erik_response.xls]
2015-02-11 Adding artwork from final files before manufacture
    [05_10_2014_pc049a_toplevel_39_a16-5.brd, A 09 10 2014 pc049a_toplevel_40_a16-5.brd, B_09_10_2014_pc049a_toplevel_40_a16-5.brd, page6.csv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]
2015-02-12 Minor changes following PCB checking
    [pc049a_toplevel_48-1-10.drl]
2015-02-12 Changing clearanges to get ground pins on DIN connectors connected to ground planes on layers 7 , 10
2015-02-23 Adding artwork after glossing and power supply capacitor changes
    [pc049a_toplevel_50_gloss1-1-10.drl, pc049a_toplevel_51-1-10.drl]
2015-02-23 Tidying artwork
    [pc049a_toplevel_48-1-10.drl, pc049a_toplevel_50_gloss1-1-10.drl]
2015-03-23 Checking in files before copying to GIT
    [PC048A.drl, PC048A_PTH.drl, pc049a_bom.xlsx, pc049a_checklist.xlsx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]
2015-03-27 Comissioning boards.
    * Took pictures of assembled boards.
    * Exported netlist from Circuit schematic.
    * Changed clocks to be 31.25MHz IPBus clock.
    * General tidying. Unfortunately, latest design doesn't respond to "ping"....
2015-03-30 Edited UCF to specify termination of some of the LVDS lines.
    Edited pc049a_top.vhd in order to only build the IPBus ( not the White Rabbit ) cores by default. Reduces power dissipation and keeps chip cooler.
2015-05-26 Comitting changes for working demo version
    * marocInterface_rtl.vhd - detects the falling edge of status from marocADC
    * circuit to detect falling edge of status hdl/fallingEdgeDetect_rtl.vhd
2016-01-29 Checking in current code.
    Some documentation changes
    Changed Slow control shift register to have optional reset before shifting data.
    ( Still at least one bug - doesn't store data shifted out of MAROC correctly )
    Added register stages to risingEdgeDetect
2016-03-01 Adding more Python readout scripts.
    takeMarocData - multi-threaded top level script to take data.
    MarocReadoutThread , MarocHistogrammingThread , MarocRecordingThread - classes that inherit from Threading class
2016-03-02 MarocConfiguration - class that writes to registers in FPGA , including register that controls interface to MAROC slow control. Reads data to write to slow control from CSV file.
    takeMarocData.py - passes number of events to readout thread. Passes file name to recording thread. Waits for threads to finish before exiting
    MarocRecording.py - eventually sorted out how to record to a ROOT file. Inefficient at the moment.
    MarocSC.py - started to add ability to store register values in CSV file as well as contents of MAROC SC registers.
    MarocHistogrammingThread.py,MarocReadoutThread.py,MarocRecordingThread.py,MarocUnpackingThread.py - when readout thread reaches event limit it passes a "specia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
2016-03-03 - MarocConfiguration.py - passes configuration file name to MarocSC object and reads from configuration file.
    - MarocHistograms.py - replaced print statements with logger.info / logger.debug
    - MarocSC.py - debugged so can now read flags, parameters and register values from configuration file.
    - takeMarocData.py - added command line switch to set configuration file name
2016-03-03 Checking in example configuration file.
    [testADC_marocSC.csv]
2016-03-17 marocInterface_rtl.vhd - Added external trigger from GPIO header as well as from DIN41612 connectors
    marocTriggerGenerator_rtl.vhd - added attributes to prevent synchronization steps being optimized to a shift register
2016-03-18 Added some protection against buffer over-run. Unfortunately doesn't work at start of run ....
    [testADC_marocSC.csv]
2016-03-24 Committing changes before moving to Git
    [pc049a_db.xlsx, pc049a_lemo_db_12.brd]
2016-04-15 Checking in files before another attempted Git migration.
    More firmware development:
    Took copies of firmware/hdl/i2c_master_* to avoid having to pull in.
    Wrote some test-benches for data mux code:
    dummyMarocADC_behavioural.vhd
    marocTimeStampMuxArray_tb.vhd
    marocTimeStampMux_tb.vhd
    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
    [pc048a_data_format.ods, pc049a_db.xlsx, pc049a_db_1per_line.csv, pc049a_db_1per_line.xlsx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]
2016-12-01 Connected trigger output to GPIO pin
    [testADC_marocSC.csv]
2026-06-16 Committing changes to move from Python2 --> Python3
    [testADC_marocSC.csv]
2026-06-18 Adding files that probably(possibly) should be added to Git
    [testADC_marocSC.csv, testADC_marocSC_6V.csv, testADC_marocSC_Chiara.csv, testADC_marocSC_rpc.csv]

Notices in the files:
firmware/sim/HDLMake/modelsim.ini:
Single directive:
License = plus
